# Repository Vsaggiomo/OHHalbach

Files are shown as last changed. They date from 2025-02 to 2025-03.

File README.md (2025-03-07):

# Open Hardware Sweepable Halbach array

Floris Dekker, Julia Krug, Vittorio Saggiomo

IMPORTANT: THIS IS STILL A WORK IN PROGRESS

This research was done with the support of Open Science NL, Open Science Fund 23-1 - project OHEPR  

For NMR, MRI or EPR, a Halbach array cylinder has a few advantageous characteristics to use in the magnet design. In a perfect Halbach cylinder, the B0 inside is highly homogeneous, and stronger than without this array. The stray field on the outside on the other hand is quite weak. However, this assumes an infinitely long cylinder where the magnetic ring consists of an infinite amount of segments magnetized in a different direction. In practice this is not possible, but with sufficient height and enough rotated cube magnets, an approximation can be achieved. Using a single ring of cube magnets, this means there will be, theoretically, a trade off between homogeneity (more magnets = higher field homogeneity) and strength (more segments, i.e. more magnets with smaller size = lower field strength). 
In the case of EPR, the Halbach array cylinder offers another advantage.(1) For this technique it is necessary to sweep the magnetic field, and with multiple rings of Halbach cylinders, the net magnetic field can be changed by rotating the rings around each other. In order to prevent the direction of the magnetic field to change, two equally strong rings need to be rotated in opposite direction to cancel out the orthogonal components of the vector. Therefore, when constructing such a system, it is important to be able to construct two different sized rings that are equal in strength. As the simulated field strength does not accurately predict the B0 of the constructed ring, due to practical limitations, it is necessary to investigate the relation between the simulated and the real strength of B0.

### how did we get there? 

read [simulation and characterization](simulation.md) 

read [FEMM simulation](femm.md) 

go to the 3D printable [STL files](stl) for the 3 rings array 

### results 
For this experiment, a prototype is designed for a sweepable Halbach magnet that consists of 3 layers of 5 stacked Halbach array rings. Figure 1 shows the schematic for the design to clarify what is meant with layers and stacks, and to show the axes in relation to the magnet.

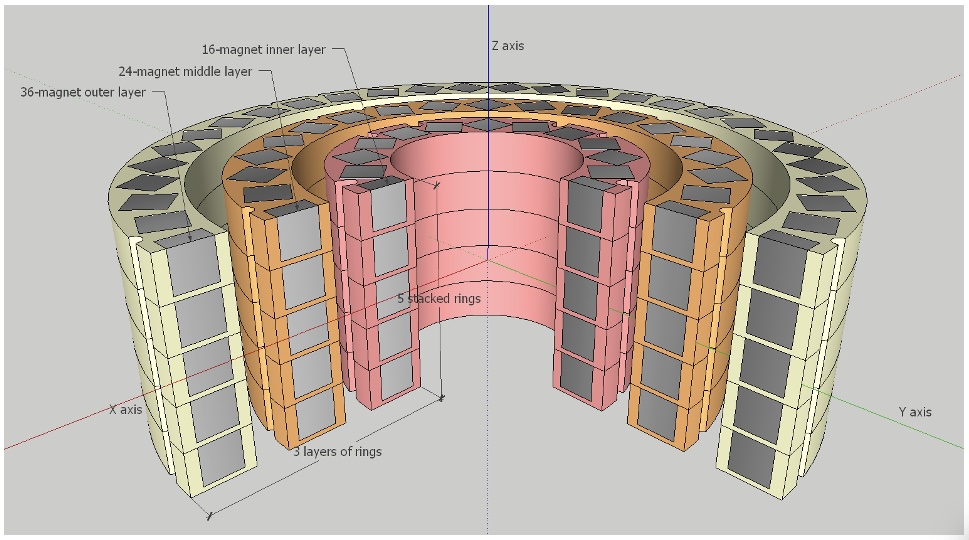
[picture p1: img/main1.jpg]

***Figure 1**. A cross-section of the EPR magnet showing the different Halbach rings. The magnet consists of 5 stacked rings with 16 magnets as the inner layer (shown in pink), 5 stacked rings with 24 magnets as the middle layer (light orange), and 5 stacked rings with 36 magnet (light yellow). The middle of the magnet is defined as (0,0,0) with the z axis (blue) running through the bore.*

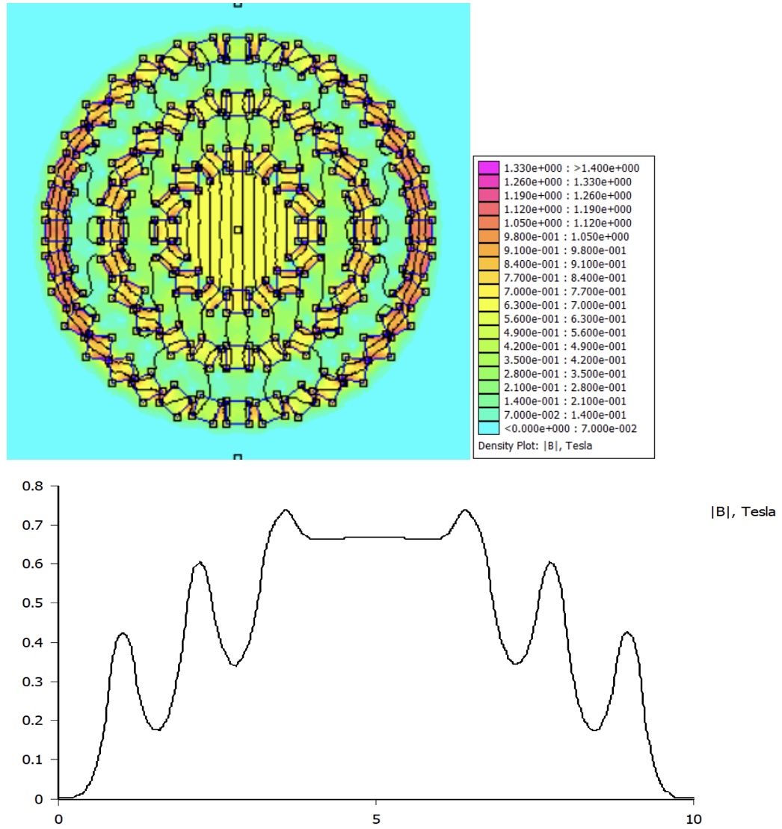
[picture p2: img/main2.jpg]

***Figure 2**: Above the colour-scaled Flux density plot of the 3 ring Halbach with all 3 rings oriented in the same direction. Below, the magnetic field strength is plotted along the middle of the Halbach array (vertical line through the middle). The field strength at (0,0) is determined using FEMM simulation to be 0.666 T.*

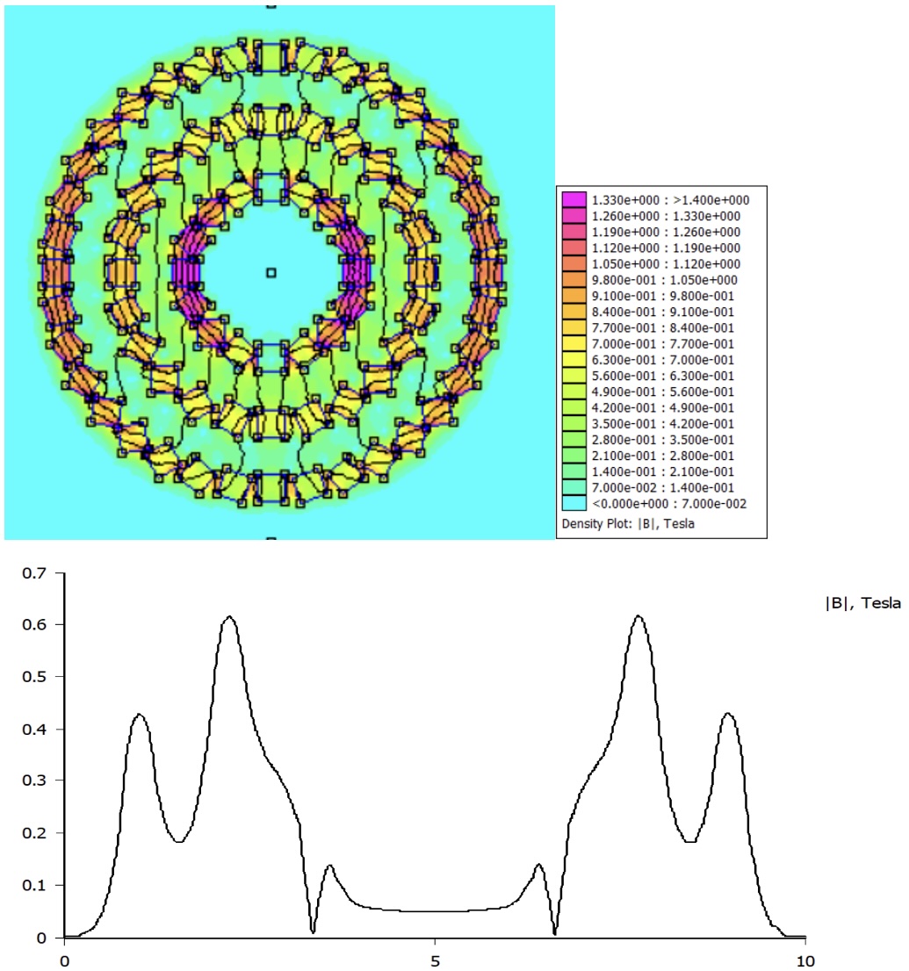
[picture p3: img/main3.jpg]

*Figure 3: Above the colour-scaled Flux density plot of the 3 ring Halbach when the outer 2 rings are rotated 180 degrees in respect to the inner ring. Below, the magnetic field strength is plotted along the middle of the Halbach array (vertical line through the middle). The field strength at (0,0) is determined using FEMM simulation to be 0.048 T.*

###Further Experiments
In future, the stacked rings for 16-magnet rings should be measured using a more precise setup for the Hall meter. Additionally, the stacked magnet arrays with 24 and 36-magnet rings still need to be constructed and characterized in a similar fashion. 
When all three layers of stacked rings are constructed, the B0 field inside should be measured, as well as the influence of rotating the layers on the field. This can be compared to the simulation of a 3-layered system.
For all three different ring designs, it will be useful to simulate different diameter rings (keeping the same amount and size of magnets) to plot the relationship between diameter and field strength. A few real world designs can be made and characterized to compare to this plot. This way it will be possible to pick a desired field strength for each ring in further prototypes.

### Acknowledgment 

We thank Sander Baas for the support. 

references: 
(1) 1.	Bauer, C., Raich, H., Jeschke, G., & Blümler, P. (2009). Design of a permanent magnet with a mechanical sweep suitable for variable-temperature continuous-wave and pulsed EPR spectroscopy. Journal of Magnetic Resonance, 198(2), 222–227. https://doi.org/10.1016/j.jmr.2009.02.010 []()

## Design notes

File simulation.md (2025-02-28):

# Simulation of the different Halbach Arrays

To investigate the accuracy of the simulation, a comparison is made between 3 simulations and their constructed counterparts. 
Case 1 is a ring that consists of 16 magnets and is designed to maximize the field strength, that is with the smallest possible diameter. A design is made that fulfills these criteria, and is then simulated. After this, the Halbach holder is 3d printed with PLA and constructed with NdFeB cube magnets of 5mm. This ring is then tested with a Hall magnetometer to determine the actual field strength. 
Case 2 is a ring consisting of 24 magnets. Considering the final design of the three ring EPR magnet, the design is not chosen to minimize the diameter. Instead a diameter is chosen that can be easily fitted in between the two other rings. Case 1 and 3 are designed with a minimal diameter possible for their geometry. Case 2 is chosen to have a diameter precisely in between this, which means that it is somewhat larger than the minimal possible. A design is made that fulfills these criteria, and is then simulated. After this, the Halbach holder is 3d printed with PLA and constructed with NdFeB cube magnets of 5mm. This ring is then tested with a Hall magnetometer to determine the actual field strength.
Case 3 is a ring that consists of 36 magnets and is designed to maximize the field strength (and thus smallest possible diameter). A design is made that fulfills these criteria, and is then simulated. After this, the Halbach holder is 3d printed with PLA and constructed with NdFeB cube magnets of 5mm. This ring is then tested with a Hall magnetometer to determine the actual field strength. 
Figures 1, 2, and 3 show the design of the separate cases as well as the results of the simulation and the measurements for the 16-magnet, 24-magnet, and 36 magnet cases, respectively.

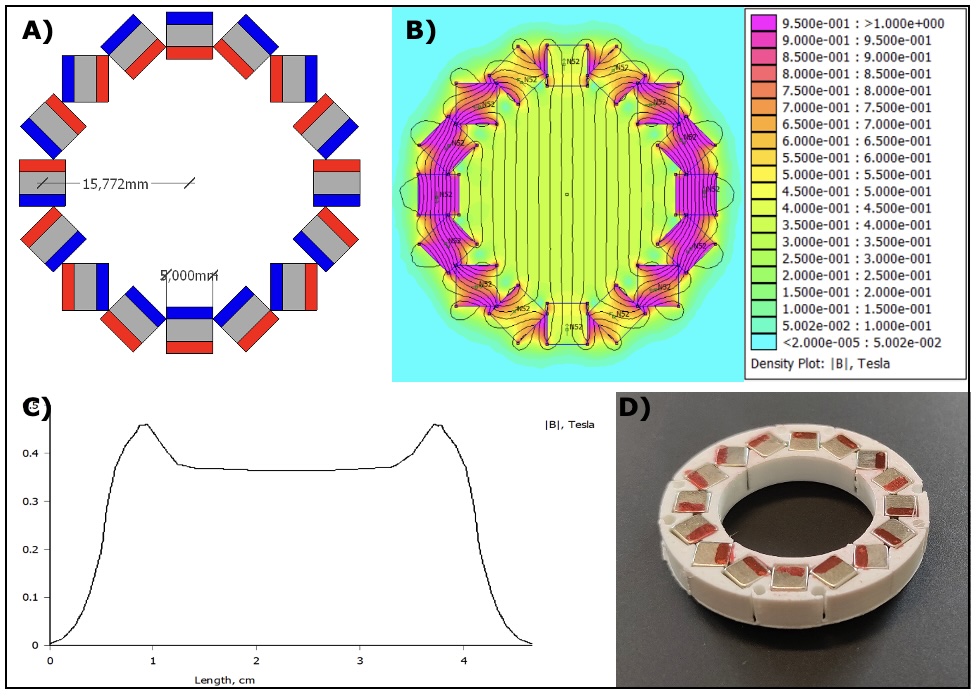
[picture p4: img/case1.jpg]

***Figure 1** A) A Halbach array containing 16 cube magnets of 5mm. The array is designed to have a minimal diameter, so that the corners of the cubes touch. This results in a radius (measured from magnet center to magnet center) of ~15.772 mm. B) Simulated magnet field of the Halbach array, using FEMM 4.2. The magnets used are N52 NdFeB square magnets. Since the simulation is 2-dimensional, an infinitely long cylinder is assumed. At (0,0) in the center of the array, the simulated B0 is 0.3624 T. C) A plot of the magnetic field density of the simulated Halbach array, running along the center of the array, parallel to the B0 field. D) Picture of the constructed Halbach ring, based on the schematic of figure 1A. The magnets used are a single layer of 5mm cube magnets made from N52 NdFeB.*

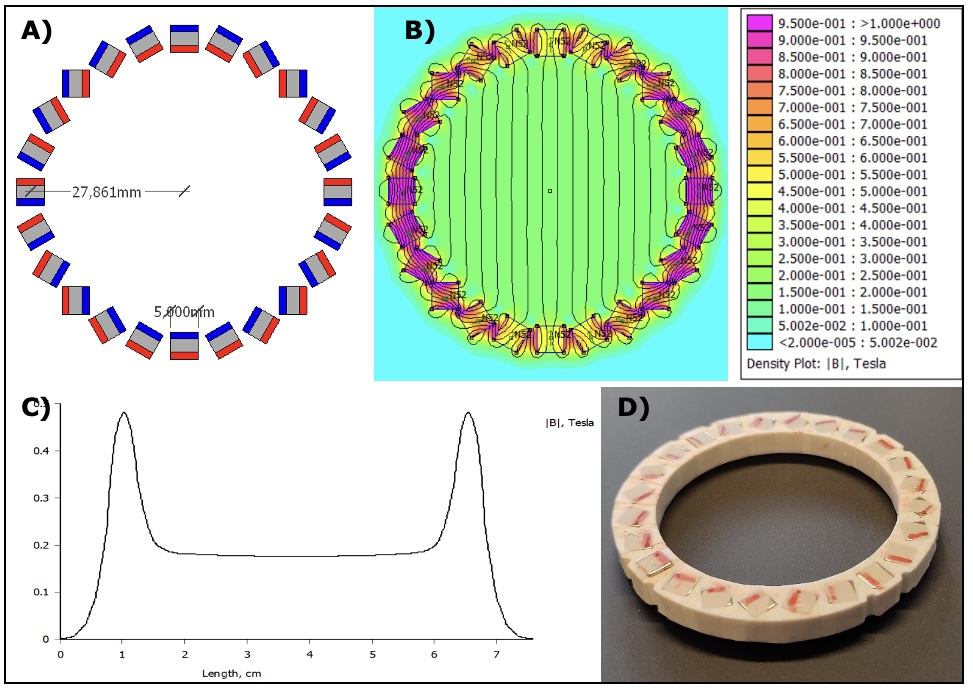
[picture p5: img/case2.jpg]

***Figure 2** A) A Halbach array containing 24 cube magnets of 5mm. The array is designed with a radius precisely in between the 16 and 24 magnet design. This results in a radius (measured from magnet center to magnet center) of ~27.861 mm. B) Simulated magnet field of the Halbach array, using FEMM 4.2. The magnets used are N52 NdFeB square magnets. Since the simulation is 2-dimensional, an infinitely long cylinder is assumed. At (0,0) in the center of the array, the simulated B0 is 0.1753 T. C) A plot of the magnetic field density of the simulated Halbach array, running along the center of the array, parallel to the B0 field. D) Picture of the constructed Halbach ring, based on the schematic of figure 2A. The magnets used are a single layer of 5mm cube magnets made from N52 NdFeB. *

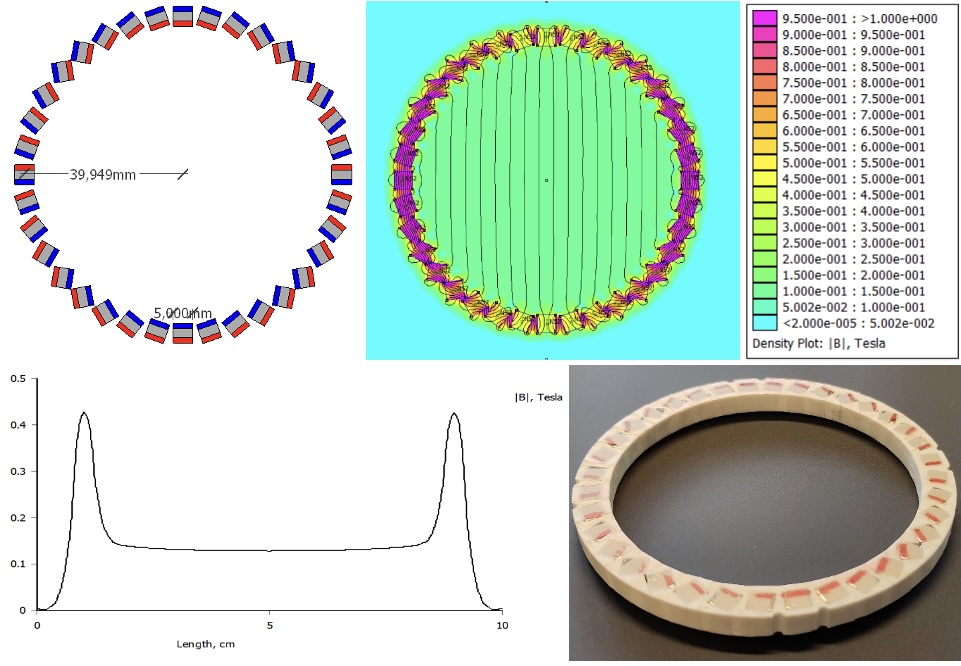
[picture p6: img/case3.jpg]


***Figure 3** A) A Halbach array containing 36 cube magnets of 5mm. The array is designed to have a minimal diameter, so that the corners of the cubes touch. This results in a radius (measured from magnet center to magnet center) of ~39.949 mm. B) Simulated magnet field of the Halbach array, using FEMM 4.2. The magnets used are N52 NdFeB square magnets. Since the simulation is 2-dimensional, an infinitely long cylinder is assumed. At (0,0) in the center of the array, the simulated B0 is 0.1280 T. C) A plot of the magnetic field density of the simulated Halbach array, running along the center of the array, parallel to the B0 field. D) Picture of the constructed Halbach ring, based on the schematic of figure 3A. The magnets used are a single layer of 5mm cube magnets made from N52 NdFeB.*

## Measuring Field Strength with Hall sensor
For each ring size (16, 24, and 36 magnets), 5 rings were constructed. Using the handheld hall magnetometer from metrolabs, the strength of each ring was measured by moving the sensor through the middle of the ring and noting down the maximum recorded strength. To account for temperature fluctuation during the measurement, each measurement was repeated twice after all rings had been measured. The results of these measurements are given in Table 1:
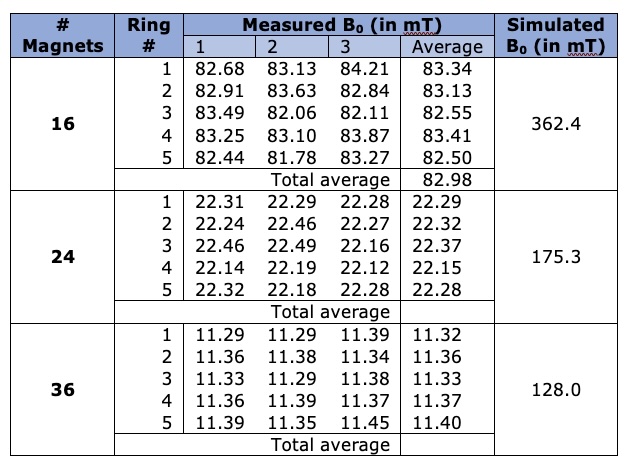
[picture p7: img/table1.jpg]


## Characterization of stacked ring
A holder was printed for the 5 16-magnet rings to stack the layers. The holder was designed in such a way that the rings are fixated on top of each other with minimal distance, and to prevent rotation of the individual rings. After stacking the rings on top of each other, with poles in the same direction, the stacked ring was measured along the z-axis using the Metrolabs magnetometer. The result of this is shown in Figure 4.

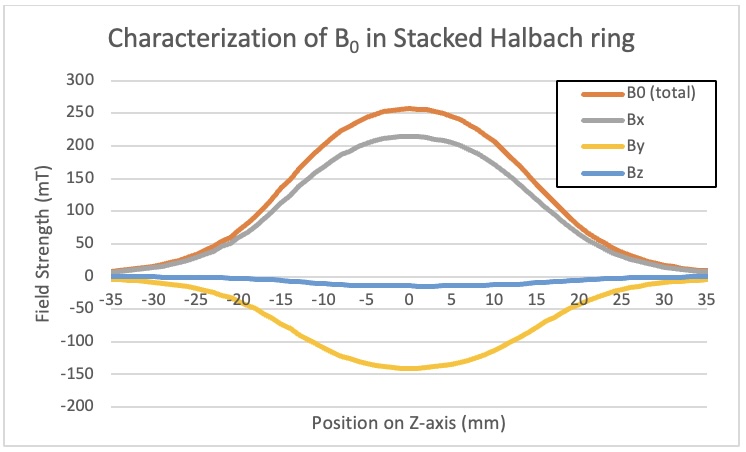
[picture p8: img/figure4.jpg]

***Figure 4**. The field strength measured along the central z-axis of a stacked Halbach ring. The ring consists of 5 16-magnet rings on top of each other, oriented in the same direction. The distance between the magnets in the z-direction is 0.6mm. The magnetic field profile shows a relatively symmetric curve of the field strength, yet there is no homogeneous plateau in the middle. Since the individual contribution of the Bx and By field is dependent on the arbitrarily used rotation of the Hall sensor, the total B0 is the most important value. The non-zero value of Bz indicates a small offset between the stage and the Halbach array.*

## Discussion and Conclusion
Comparing the simulations of the three different ring designs, the magnetic field becomes weaker, if the diameter of the ring becomes larger. This is to be expected. While a Halbach array can be scaled up without changing the magnetic field strength, a larger ring using more, evenly-sized magnet cubes, becomes relatively thinner and thus becomes weaker. In real life, the difference becomes even larger, as not only do the rings get thinner, the ratio between height and diameter also becomes smaller, deviating further from the simulated infinite cylinder. The 16-magnet ring reaches ~23% of the simulated field strength, for the 24-magnet ring and the 36-magnet ring this is only ~13% and ~9% respectively. 

The measurement of the stacked ring shows that the field strength already drastically increases when 5 rings are stacked on top of each other. The maximum B0 increases from ~23% of the simulated field strength to ~71% (257 mT). Stacking more rings on top of each other will most likely increase this further, but will yield diminishing returns. Noteworthy, the magnets in the rings are not touching, but separated in the z-direction because of the design of the 3d printed holders. Even if one would extend the cylinder infinitely, the magnets would only occupy 89% of the possible space, so it is unlikely that the field strength would reach higher than 89% of the simulated field using the current design.

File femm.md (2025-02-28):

# Summary FEMM Simulation 

For construction of an EPR magnet with several layers of Halbach rings, it is important to accurately predict the field strength of an Halbach ring with a specific geometry. Using FEMM 4.2, Halbach rings with different parameters are simulated and compared for their field strength at the center (B0(0,0)). For a fixed size and material of square magnets, the B0(0,0) depends on the number of magnets in the ring and the radius and closely follows the following formula:  B0(0,0)=(#magnets*x)/r2, where r is the radius of the ring and x a number that depends on the magnetization and geometry of the magnets, among other things. This correlation between these parameters and the magnetic field strength can be used to more easily design a Halbach system suitable for EPR spectroscopy.

## Background

Electron Paramagnetic Resonance spectroscopy (EPR) depends on a magnetic field sweep at a fixed frequency. Therefore, an EPR system needs a way of regulating and changing the B0 field of the magnet. Most EPR setups use a secondary electromagnet for this, but there are different options for this. Bauer et al. (1)designed a magnet for EPR spectroscopy that works with three layers of stacked Halbach cylinders. By turning the rings, the magnetic field inside can either add up or (partially) cancel out to modulate the magnetic field. 
An Halbach array cylinder has the advantage that the magnetic field inside is relatively strong and homogeneous. In the EPR system from Bauer et al.(1) a field homogeneity of ~1000 ppm is reached, which is homogeneous enough for EPR spectroscopy. Because EPR spectroscopy often uses a microwave generator that operates at a very precise wavelength, it is important to design the magnet with the necessary field strength so that the electron resonance frequency matches that of the microwave generator.
For such a design, there are 2 parameters that can be very easily adjusted to influence the strength of the B0 field: the radius of the cylinder and the number of magnets used. The correlation between these factors and B0, can be investigated using simulation software. FEMM 4.2 is such a simulation software for magnetic fields. While it reduces the setup to 2 dimensions, and this ignores effects such as the ends of a 3D cylinder, its ease of use and fast results make it a useful tool to explore the different geometries of 2D Halbach rings, and their field strengths. 

## Materials and methods
For the simulation of Halbach rings, FEMM 4.2 was used. A custom script is written for the construction of a Halbach array with different parameters. For each simulation, a Halbach ring was constructed with 1x1 square magnets made of N50 sintered NdFeB magnets. As Halbach arrays scale linearly, distance is a dimensionless number in the simulation but it is assumed to be in cm.
The field strength of each ring is determined by picking the center of the ring (0,0) and reading out the field strength in Tesla at these coordinates.

## Results and discussion
###Influence of ring radius on field strength

For a given number of magnets, rings with different radii were simulated. A series of rings were made for 4, 8, 12, 16, 24, 28, 32, and 36 magnets. The radii ranged from 1 cm to 12 cm, although the amount of magnets in the ring put restrictions on the minimum radius for some series. The results of these simulations are shown in Figure 1. The field strength at (0,0) for a Halbach ring with varying radius and number of magnets in the ring. All simulations used 1x1cm square magnets made out of N50 NdFeB. The dotted lines are fitted trendlines for each series of radii. For the rings with more magnets, the data starts at a higher radius, because otherwise the magnets would overlap.

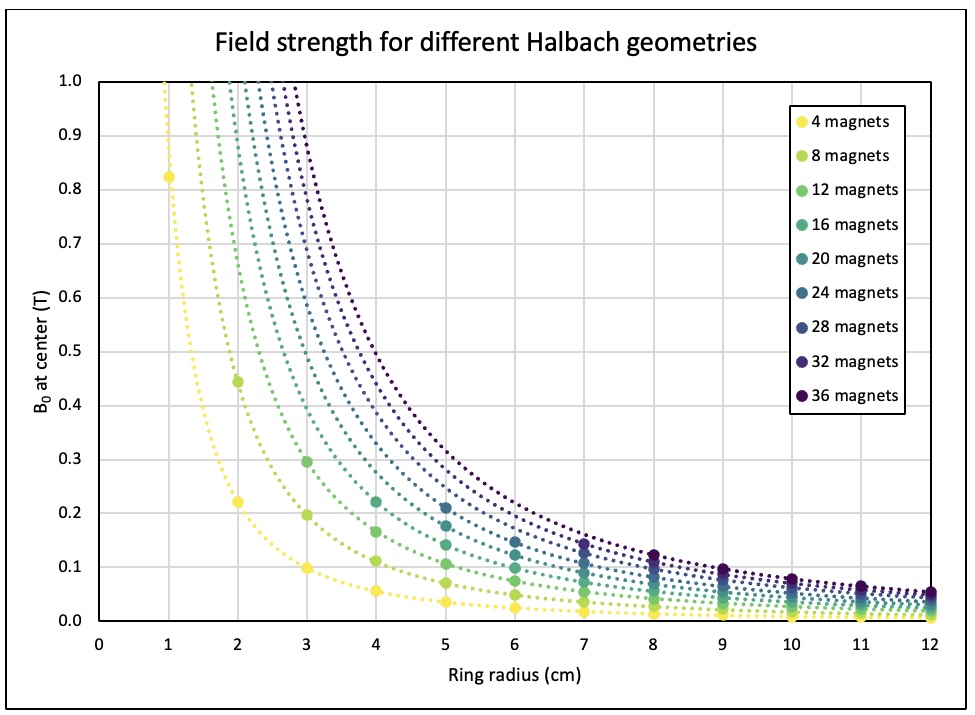
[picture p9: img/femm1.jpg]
 
***Figure 1**. The field strength at (0,0) for a Halbach ring with varying radius and number of magnets in the ring. All simulations used 1x1cm square magnets made out of N50 NdFeB. The dotted lines are fitted trendlines for each series of radii. For the rings with more magnets, the data starts at a higher radius, because otherwise the magnets would overlap.*

For a ring with differing radius, the internal area depends on the r2. If the ring contains a fixed amount of magnets, the total magnetic field is constant, only spread out over a different area. The simulated results of Figure 1 were therefore fitted with the following formula: B_0 (0,0)=A/r^2  with r the radius of the ring and A a varying number. The value of A was determined by comparing the calculated data with the simulated one, taking the sum of the residual squared (SSR) and minimizing this by varying the value of A. For every series except for the 4 magnet rings, SSR  was less  than 0.000001 indicating a very close fit. Since the simulation, based on the finite element method, is not a perfect simulation of reality but a proximation with several iterations, this value of SSR could well be due to the limitations of the simulation. 

For the 4 magnet series, the B0 differs from the expected value at r=1. This is also the only simulated ring where the magnets exactly touch. If this data point is left out because of this unique condition, the SSR approaches 0 for this series too. In Table 1 the value of A for each series is given, as well as the SSR.

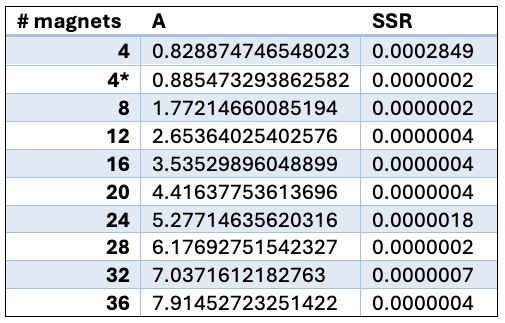
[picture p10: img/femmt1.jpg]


**Table 1**. The different values of A for Halbach rings with different numbers of magnets, and the sum of the squared residual. 4* is without the ring of 1 cm.*

###Correlation of number of magnets and field strength

The value of A for the different ring series depends on the number of magnets in the ring. A quick glance on the values in Table 1 suggests a linear correlation between the number of magnets and the value of A. This makes sense. If every magnet generates an equally strong magnetic field, the total field strength is just the result of adding all these individual contributions together. 
But this is only true if every magnet in a Halbach array contributes equally to the internal magnetic field, regardless of orientation in the ring. To test this hypothesis, a series of rings were simulated with a fixed radius (12 cm), but with different numbers of magnets in the ring. Similarly to previous experiment, the field strength was determined by looking at the B0 at coordinates (0,0). These results are shown in Figure 2.

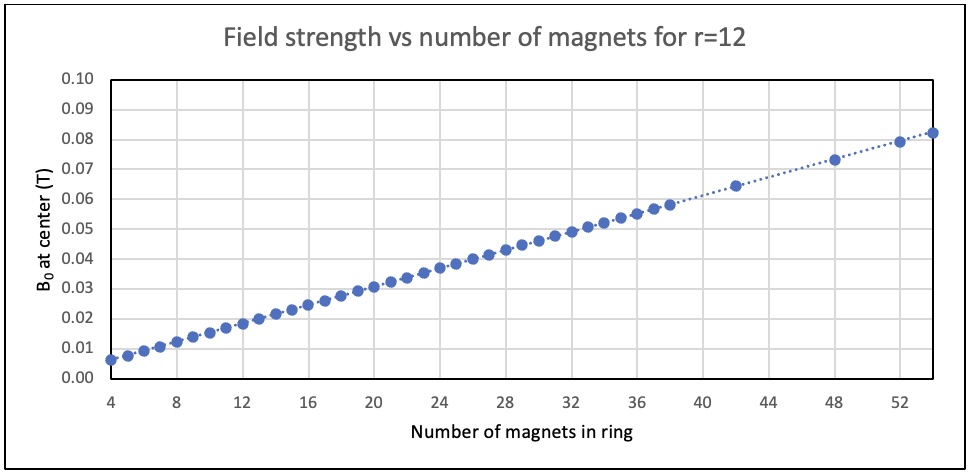
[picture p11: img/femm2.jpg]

***Figure 2**. The field strength at (0,0) for a Halbach ring with a fixed radius of 12 cm vs the number of magnets in the ring. The minimum amount for a Halbach array ring is 4 magnets and for more than 55 magnets at this radius, the magnets would overlap. A linear trendline is plotted (dotted line) to fit the data. *

A linear trendline is fitted by plotting a fit function (B0=#magnets*A), calculating the difference between the simulated data and minimizing the sum of the squared residual by varying A. This gives a value of A=1.5328*10-3, meaning that every magnet would contribute 1.5328 mT to the B0 at (0,0).
If this formula would be a perfect fit the following would be true:  (B_0 (0,0))/(A*#magnets)=1.  However, calculating this for every data point, the true value ranges from 1.0056 at Nmagnets=4 to 0.9913 at  Nmagnets=55. So while this formula can predict the field strength within an error margin of 1%, it is not a perfect description of the B0, and it seems that with more magnets, the individual contribution slightly decreases.

##Conclusion 
A custom script was written to easily construct Halbach rings in FEMM 4.2 with the desired parameters. With this, a comparison was made between the radius and number of magnets of the Halbach ring vs the magnetic field strength at the center. A relation was found between the field strength at the center and the radius of the ring according to the following equation:
B_0 (0,0)=x/r^2  						(1)
Where x is an unknown value differing in between Halbach geometries.
Plotting the B0 against the number of magnets in the ring gives an almost linear relation for a fixed diameter. Combining this knowledge with equation 1, we get the following equation to approximate the field strength at the center for a 2D Halbach 
B_0 (0,0)≈(N_magnets*x)/r^2 					(2)
Here x certainly depends on multiple factors, such as the material of the magnets, the shape of the magnets, and probably other factors. Considering square magnets of 1x1 cm NdFeB N50 magnets, the value of x is found to be 1.5328*10-3. While this is not a perfect description of the Halbach ring, it can be used for a reasonably accurate prediction.
Future Perspective
To further enable the design of a Halbach setup for EPR, it is important to look at the influence of the radius and number of magnets on the homogeneity of the field, and to look at the influence of magnetic material on these factors. This can be done using the same simulation and script for designing the Halbach rings. 
A more time consuming, but equally important part will be to link real life measurements of Halbach cylinders to the simulated results. Here, imperfect magnetization and magnet placement, as well as end effects introduced by a 3rd dimension will influence the results. It might be useful to look at different simulation software to investigate these effects. Microwave studio is a simulation software that is 3 dimensional, which makes it possible to study the influence of end effects of a 3d Halbach cylinder. The disadvantage is that simulating this costs a lot of computing power. 
Another aspect which is needed at some point regardless is constructing cylinders with different geometries to relate the real world results with simulated values. If there proves to be a relatively fixed factor as a difference between these two, it will already be much easier to design an EPR magnet that can operate in the desired range of field strength.

go to [FEMM script ](Halbach_construction_Open.lua)

references: 
(1) 1.	Bauer, C., Raich, H., Jeschke, G., & Blümler, P. (2009). Design of a permanent magnet with a mechanical sweep suitable for variable-temperature continuous-wave and pulsed EPR spectroscopy. Journal of Magnetic Resonance, 198(2), 222–227. https://doi.org/10.1016/j.jmr.2009.02.010 []()

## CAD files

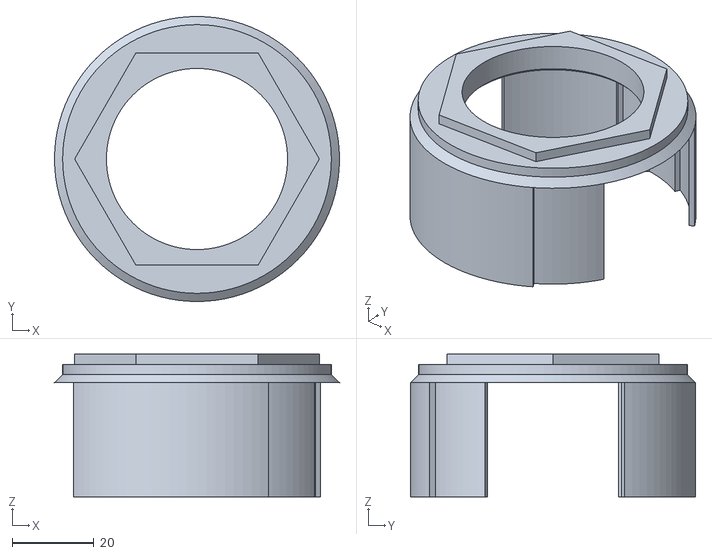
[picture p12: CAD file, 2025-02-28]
stl/24 magnet ring case top - 3 layer Halbach.stl
69.9 x 69.9 x 35.0

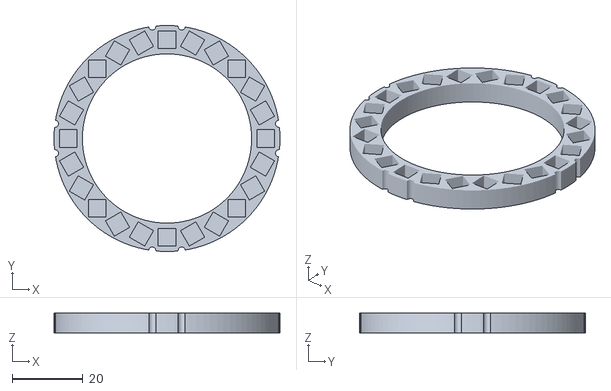
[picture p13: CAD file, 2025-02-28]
stl/24 magnet ring - 3 layer Halbach.stl
63.7 x 63.7 x 5.60

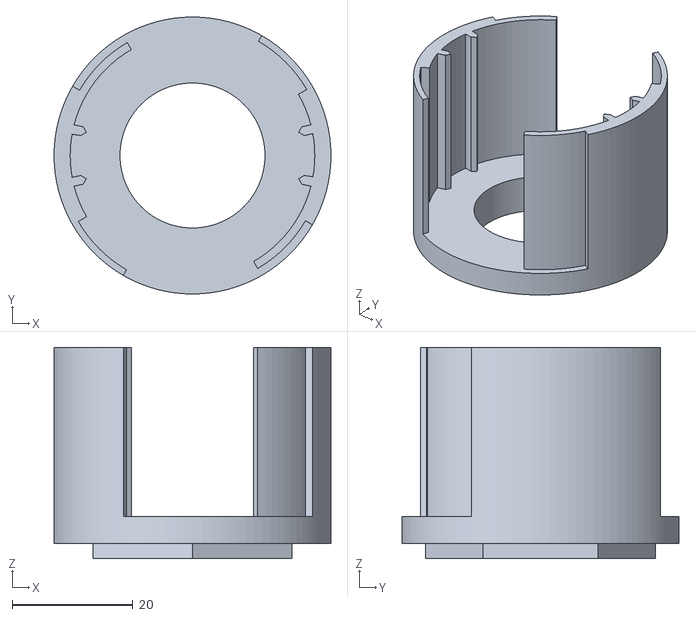
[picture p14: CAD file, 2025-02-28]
stl/16 magnet ring case bottom - 3 layer Halbach.stl
45.9 x 45.9 x 35.0

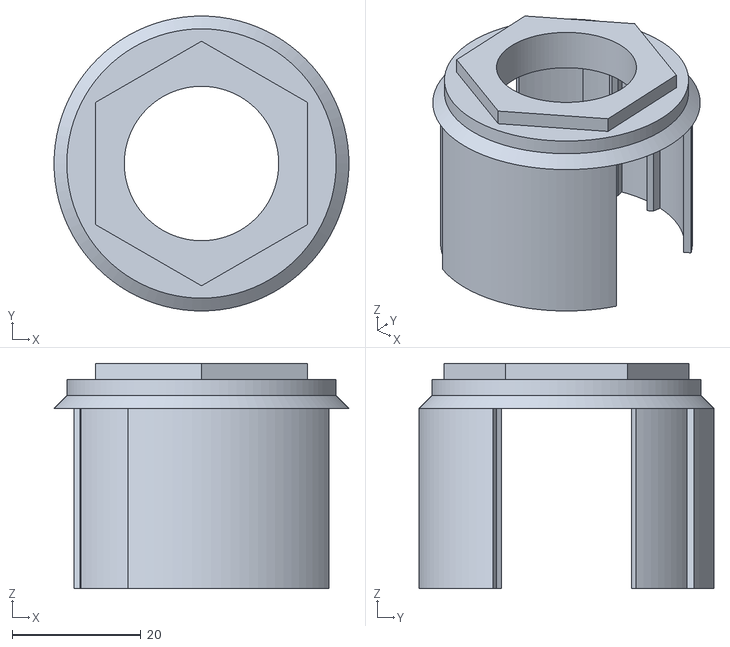
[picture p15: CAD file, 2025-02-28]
stl/16 magnet ring case top - 3 layer Halbach.stl
45.9 x 45.9 x 35.0

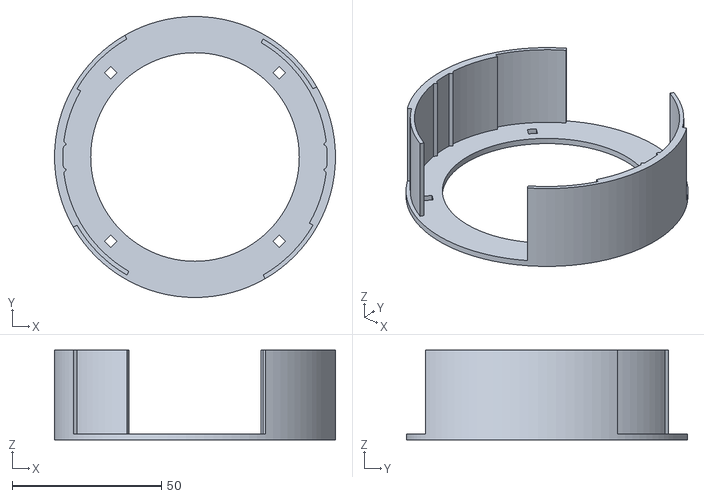
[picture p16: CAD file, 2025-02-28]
stl/36 magnet ring case bottom - 3 layer Halbach.stl
94.1 x 94.1 x 30.0

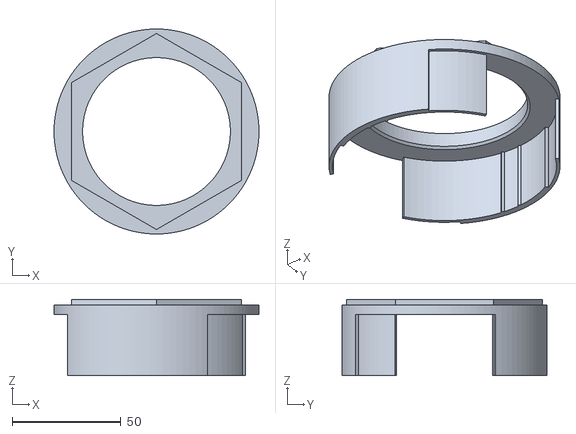
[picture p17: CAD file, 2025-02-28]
stl/36 magnet ring case top- 3 layer Halbach.stl
94.1 x 94.1 x 35.0

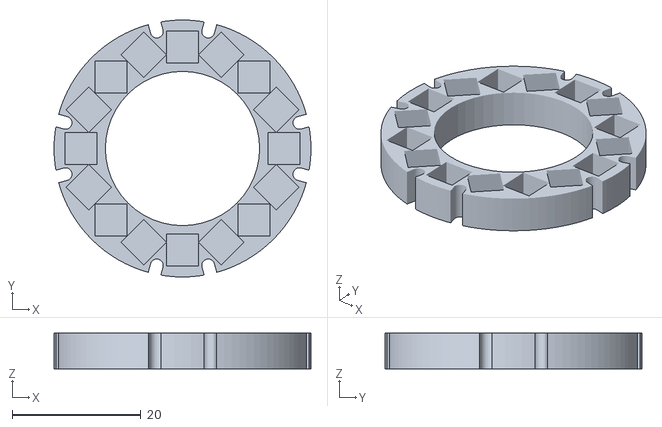
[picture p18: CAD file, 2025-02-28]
stl/16 magnet ring - 3 layer Halbach.stl
40.0 x 40.0 x 5.60

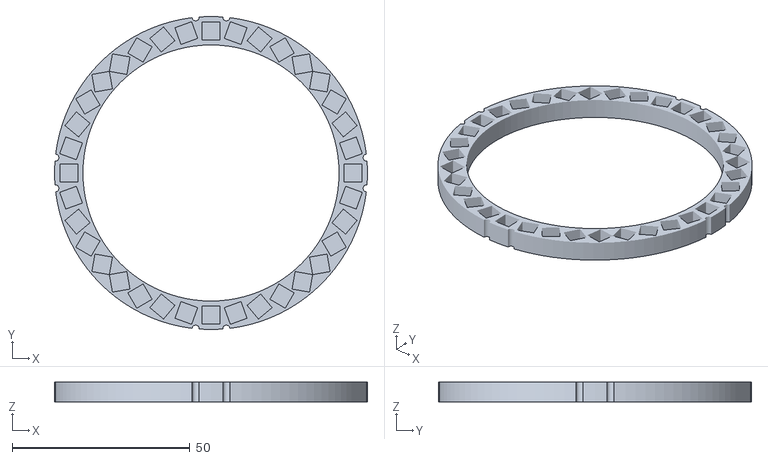
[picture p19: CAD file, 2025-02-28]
stl/36 magnet ring - 3 layer Halbach.stl
88.0 x 88.0 x 5.60

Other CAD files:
stl/24 magnet ring case bottom - 3 layer Halbach.stl
